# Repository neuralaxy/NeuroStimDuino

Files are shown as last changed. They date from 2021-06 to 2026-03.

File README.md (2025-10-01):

# NeuroStimDuino
An open source neurostimulator for students, researchers, and hobbyists interested in neuroscience

## Update for 2025 - NeuroStimDuino v3.0  launched!! :boom: :boom: 💫
Hello NeuroStim Enthusiats!! Its been a while....over the last year, we have been busy revising the design of NeuroStimDuino. The main reason for modifying NSDuino2.1 was that one of its crucial components, the high voltage DC-DC converter NMT0572SC from Murata has now became obsolete and out of circulation. Sadly, there was no alternative component that could take its place and we spend months trying to find a replacement. 

Finally we had a breakthrough, and we found another DC-DC converter IH0524 from XP Power. We had to redesign the board slightly to incorporate this Converter. But the *downside* is that the new converter only allows a compliance voltage of 35V instead of 60V available in the previous versions. How will this effect your experiments? Well, it means that now you will have to take extra effort in minimizing the skin impedance to deliver higher currents. But we have tried stimulating our arm muscles using this newer version, and it is just as effective as before. And we highly recommend using hydrogel electrodes, as we have suggested before in the [Zucchini](https://www.crowdsupply.com/neuralaxy/neurostimduino/updates/tips-on-electrode-placement) experiment. 

On the *upside*, while we were redesigning the board, we replaced the manual High Voltage slide switch with an electronic switch (see below). So now, you don't have to worry about turning ON the high voltage switch before activating the stimulator. Whenever you give the STIM command, the microcontroller will automatically turn ON the high voltage supply and once the stimulation is turned off, the high voltage supply is automatically turned off. Another benefit of adding the electronic switch is that it will minimize power consumption, since the high-voltage supply doesn't need to be always ON. Now that's smart😎.

Replaced_Slide_Switch_with_SSR

All the other features from NSDuino2.1, like ramping stimulation intensity, touchproof conenctors, etc. have been carried over to NSDuino3.0. Late in September 2025, we launched NeuroStimDuino v3.0 abd shipped out the first batch to our distributor Mouser. A big shout out to 📢 CrowdSupply and Mouser for consistently supporting us over the years. Some of you might have already received the newer version. Try it and let us know how it goes.  

## Important update for 2023
In January 2023 we have launched NeuroStimDuino v2.1, which comes with additional features and improved functionality than its predecessor NeuroStimDuino v1.0. 

NeuroStimDuino_v2 1

Here is a list of important upgrades for NeuroStimDuino v2.1 (NSDuino2.1): 
* Choosing between symmetrical and asymmetrical waveform shapes is now done entirely in software. In NeuroStimDuino v1.0, to switch from symmetrical to asymmetrical waveform, you had to change the jumper (J5, J6) as well as call the `SYMM` command. In NSDuino2.1, its handled entirely by software and the jumpers have been removed. In the default asymmetrical output mode, the anodic phase's amplitude is half of cathodic phase's amplitude and the duration of anodic phase is double that of the cathodic phase (to ensure charge balance). This ratio can be changed by modifying the firmware.

* NSDuino2.1's I<sup>2</sup>C address is now stored on EEPROM. So, whenever you assign a new I<sup>2</sup>C address to NSDuino2.1 using the `ADDR` command, it will get stored permanently and will be recalled at power-on reset. This is especially helpful when communicating with multiple NeuroStimDuinos. In NeuroStimDuino v1.0, the address would reset to the default value (0x1A) everytime the board was turned on and you would have to painstakingly re-assign the new addresses each time. With NSDuino2.1 the new address only needs to be set once and it will store it on-board its EEPROM.

* Many of NeuroStimDuino v1.0 users (who are acutally scientists!!) have asked whether it is possible to ramp up and down the stimulation intensity? Ramping is used in neurostimulation research to avoid painful sensations allow smoother transitions between movements when applying electrical stimulation. With NSDuino2.1, we have also expanded our software (Arduino) library and now provide the option to Ramp Up and Down the stimulation intentsity. When you enable ramping by using the command `RAMP 1`, the stimulation intensity will gradually increase from 0 to the desired level over a 1 second interval. At the end of stimulation, the stimulation intensity will gradually decrease to zero over a 1 second interval. There are some caveats to using ramping: 
  * In the scientific literature, ramping is usually done by increasing/decreasing the current amplitude. While this is doable, by changing the counts of our on-board digital potentiometer, it would require multiple SPI calls between the MCU and potentiometer which will introduce delays. Instead, we are performing ramping by gradually increasing the stimulation pulse-width. This is handled entirely by the MCU and hence it is more accurate. Additionally, it has the same effect as changing the stimulation current, so it won't affect the outcomes of your experiments. Refer to the below gif to understand how ramping essentially works:
  
  NSDuino_Ramping_gif
  
  * Currently, ramping only works for finite stimulation intervals. This means the `Stim Indefinitely` flag of the `STIM` command must be set to `FALSE`. An example code snippet is as follows:
  
  ```
  RAMP 1          // Turn ON ramping on channels 1 & 2
  STIM 1 5 0      // Stimulate on channel 1 for 5 sec, stim indefinitely flag = 0
  RAMP 0          // Turn OFF ramping on channels 1 & 2
  ```
  * Ramping can also be deployed in NeuroStimDuino v1.0. This would require a firmware update. We will post an upgraded firmware for NeuroStimDuino v1.0 on our repository in a few weeks time. Feel free to reach out to us for any queries regarding ramping

* Additional minor modifications:
  * We removed the bi-color(red/green) LEDs to indicate when channels 1 and 2 are stimulating, with regular monocolor LEDs. These still function in the same way
  
  LEDs_changed

  * We changed the onboard cable connectors for Channels 1 & 2 with new ones that are compatible with our stimulation cables and you no longer need to remove the cable shroud or sheath cover. This will hopefully help reduce the hassle during setup and the touchproof connectors will offer additional safety during use.
  
connector_with_shroud

# Getting Started Tutorial for NeuroStimDuino v2.1
**_Important:_** For instructions on getting started with NeuroStimDuino v1.0, please click [here](https://github.com/neuralaxy/NeuroStimDuino/blob/main/NeuroStimDuino%20v1.0%20Getting%20Started.md#getting-started-tutorial-for-neurostimduino-v10)

* To get started, first and foremost familiarize yourself with NeuroStimDuino pinout and board layout below:

NeuroStimDuino_v21_Pinout_Diagram png

NeuroStimDuino_v21_Components png

* If you have ordered the NeuroStimDuino board (without the accessory pack), then you will have received the following components.

package_contents_v2 1

* You also need to order a pair of hydrogel electrodes (from any retail vendor) if you plan to stimulate a fake muscle (such as a [Zucchini](https://www.crowdsupply.com/neuralaxy/neurostimduino/updates/tips-on-electrode-placement)) or for your research.

* Finally, before you begin, please remember to review the **safety guidelines** listed at the [end](https://github.com/neuralaxy/NeuroStimDuino/blob/main/README.md#important-safety-guidelines) of this tutorial and follow the recommendations mentioned therein.  

## Hardware Setup
* The battery holder included requires two 18650 Li-ion batteries (not included) to be connected in series. The battery holder allows the batteries to be oriented in series or parallel connection. Unfortunately, the battery holders we shipped only have Chinese labels to indicate the series or parallel oritentation. Make sure you connect the batteries in series (as shown below) and not in parallel. Alternately, you can power NeuroStimDuino using your own battery source between 6-20V. We do not recommend powering NeuroStimDuino using an AC-DC adapter. However, if you must use an adapter, then you need an adapter with atleast 2 Amps output rating

battery_holder

* The High-Voltage Power Switch S3 turns ON/OFF the +/-72V DC-DC converter (NMT0572SC). When using NeuroStimDuino for the first time we recommend starting with the switch in OFF position. Afterwards, once you are ready to stimulate then flip the switch ON. That way even if you accidentally turn ON the stimulation, it will not have any effect because the high-voltage source will be OFF. Plus it will also help extend battery life. 

power_switch

* To control NeuroStimDuino using an Arduino Due or Mega, stack NeuroStimDuino on top of the Arduino board by aligning the hearder pins, as shown below.



* Once the hardware setup is complete, the amber or yellow Emergency-OFF LED will remain continuously ON. Also TEST_LED1 and TEST_LED2 will start blinking at a rate of 5 blinks per sec.



## Software Setup
* Next, you will need to download the latest version of our [Arduino library](https://github.com/neuralaxy/NeuroStimDuino/tree/main/Software/NeuroStimDuino). Read the full update [here](https://www.crowdsupply.com/neuralaxy/neurostimduino/updates/arduino-library-released) and remember to install the [SerialCommands library] (https://github.com/ppedro74/Arduino-SerialCommands) from Pedro Pereira. Next, upload the example code NeuroStimDuino_SerialControl.ino onto the Arduino.  

* To write instructions to control NeuroStimDuino, you will use the Serial terminal that is in-built Arduino IDE (Tools > Serial Monitor). Once you open the Serial Monitor, set the baudrate to 115200 bps and add "CR+LF" at the end of each command. When you power either the Arduino or NeuroStimDuino board via the DC plug, you will see test LEDs 1 & 2 flashing on the NeuroStimDuino board. These LEDs are flashing with the default stimulation frequency of 10Hz. Now you can enter some example commands into the Serial Monitor, one command at a time and then press enter.

* After uploading the example code NeuroStimDuino_SerialControl.ino and making the connections as above, when you first open the Serial terminal you will see the following welcome message. This mean that a successful connection between Arduino and NeuroStimDuino has been established. It will also give a readout of the current stimulation parameters for each channel. 

Welcome_message

* You can type in some example commands into Serial Monitor and change the settings for the stimulator (type one statement at a time). Also, the commands are case-sensitive, so type it in all caps. 
```
FREQ 1 20        // This will set Channel 1's frequency at 20Hz. You will see the TEST LED1 blink at this new frequency
FREQ 2 50        // This will set Channel 2's frequency at 50Hz. You will see the TEST LED1 blink at this new frequency
AMPL 1 15        // Set Channel 1 intensity 15mA
DURN 1 500       // Set Channel 1 pulse duration at 500 uSec
ENAB 1 1         // This will enable Channel 1 of the stimulation. By default, both channels are enabled at reset
STIM 1 20 0      // This command will turn on stimulation on Channel 1 for 20 seconds. Ensure that the High Voltage Power Switch is ON. 
                 // You will see a Red-Green LED (labelled Ch. 1) blink  very briefly (for 500us), every time the stimulation is generated (i.e, 20  times/sec)
```

## Moving forward

* This completes this introductory tutorial. From here on, if you would like to connect cables and electrodes and actuatlly stimulate a fake Zucchini muscle, then follow the setup instructions shown in our [April Update](https://www.crowdsupply.com/neuralaxy/neurostimduino/updates/tips-on-electrode-placement) published on CrowdSupply. 

* If you want connect multiple NeuroStimDuinos together and control them using a single Arduino, then look up the steps and instructions posted [earlier](https://www.crowdsupply.com/neuralaxy/neurostimduino/updates/controlling-multiple-neurostimduinos-on-a-single-i2c-bus). Note that with NeuroStimDuino_v2.1, when you change the board's I<sup>2</sup>C using the `ADDR` command, the new address is saved on-baord its EEPROM and will be recalled even after reset. It is the User's responsiblity to reset the default I<sup>2</sup>C to `0x1A` if they wish to. 
 
* <br />**One important change** required in hardware when stacking 2 or more NeuroStimDuinos is to disconnect pins 5 & 6 on JP3. Another way to identify these pins is that they normally connect with PWM pins 9 and 10 on Arduino Due or Mega. The reason for this is that these pins can also be used to drive TEST_LED1 and TEST_LED2 of NeuroStimDuino. Therefore, if you connect them together on 2 NeuroStimDuinos, the LEDs will not function properly and can be confusing. Hence, to avoid any cross-talk, its best to fold these pins out of the way as shown below.



* We hope you enjoy tinkering with NeuroStimDuino and use it for all your neuroscience experiments. If you face any issue with the device or are stuck anytime, feel free to write to us on contactus@neuralaxy.com or submit an issue here. 

## Important safety guidelines:
* NeuroStimDuino is not an FDA approved product for clinical use and it is intended for **RESEARCH PURPOSES ONLY**. 
* NeuroStimDuino is not intended for human use or animal use, without receiving prior approval from a local ethics committee such as Institutional Review Boards and Institutional Animal Care and Use Committees  
* Under no circumstances, should the stimulation electrodes be placed across the chest or close to the heart
* NeuroStimDuino requires an external DC input voltage from 6-20V to operate. We **strongly** recommend to use an external battery for this and avoid the use of an AC adapter or anything that's plugged into the AC mains
--->

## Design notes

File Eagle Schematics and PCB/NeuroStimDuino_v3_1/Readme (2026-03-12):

Eagle schematics, BOM and assembly files for version 3.0 of NeuroStimDuino

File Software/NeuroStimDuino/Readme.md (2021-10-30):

## I2C Library for NeuroStimDuino
NeuroStimDuino can be controlled by an external microcontroller such as Arduino Due or Mega using the I2C interface, with NeuroStimDuino acting as I2C slave device (default address = 0x1A). Pull-up resistors for I2C communication are already placed onboard NeuroStimDuino and hence additional pull-up resistors are not required. A list of Opcode-style commands can be used to configure different parameters of stimulation waveform such as frequency, amplitude, etc. Each I2C message should have following structure:

- Byte 0 indicates the number of bytes that will be transferred
- Byte 1 is the Opcode command from the instruction set below for the stimulation parameter that will be modified
- Byte 2 is the channel number (1 or 2) that will written to or read from
- Byte 3 is the LSB byte of the value written
- Byte 4 is the MSB byte of the value written

## Instruction Set 
| **Instruction** | **Address** | **Description** | **Acceptable Range** | 
|----------------|--------------|-----------------|------------------------|
|  AMPL |  0x01 |   Change stimulation amplitude | 0 - 25, Unit: milliAmps |
|  FREQ  |  0x02 |   Change stimulation frequency | 1 - 100, Unit:  Hz |
|  DURN |  0x03 |  Change pulse-duration of the cathodic pulse. | 0 - 2000, Unit: uSec. |
|  IDLY | 0x04 | Change inter-phase delay | 0 - 255, Unit: uSec. |
|  DELY | 0x05 | Delay to the start of the stimulation pulse in each cycle | 0 - 1/(stimulation frequency), Unit: mSec.|
|  SYMM | 0x06 | Generate symmetrical or asymmetrical stim waveform <br /> (*Note: Make sure to change jumpers J5 and J6 settings on the board*) | 1 = Symm.; 0 = Asymm. |
|  ADDR  | 0x07 | Change 7-bit I2C address | Allowed addresses = 0x08 - 0x77; <br /> program/switch_only flag = 1/0|
|  SAMP  | 0x08 | Sample current on channel 1 or 2 | - |
|  READ  | 0x09 | Read value of register for specified channel <br /> Usage: READ Channel# Address <br /> (e.g. To read amplitude of Channel 1, use "READ 1 AMPL")   | - |
|  RSET  | 0x0A | Reset NeuroStimDuino to default register values | - |
|  EOFF | 0x0F | Generate Emergency Off condition | - |
|  STIM | 0x10 | Start stimulation on channel 1 or 2 for finite duration or stimulate indefinitely <br /> Usage: STIM Channel# Seconds# Stim Indefinitely <br /> (e.g. To stimulate on Channel 1 for 5 seconds, use "STIM 1 5 0") | 0 - 255 Sec; <br /> Stim indefinitely flag = 1/0| 
|  STOP | 0x12 | Stop stimulation on channel 1 or 2 | - | 
|  ENAB | 0x14 | Enable or disable a stim. channel | 1 = Enable; 0 = Disable | 
|  WAIT  | 0x20 | Idle | - |

## Arduino Example
An example sketch is included: NeuroStimDuino_SerialControl.ino to send I2C commands to NeuroStimDuino over the serial port. Set the baudrate at 115200 bps and add "CR+LF" at the end of each command. For using this library, you will need to install SerialCommands library available from Pedro Pereira at https://github.com/ppedro74/Arduino-SerialCommands. The library will automatically switch between SDA, SCL pins (Wire) for Arduino MEGA256 and SDA1,SCL1 pins (Wire1) for Arduino Due. 

**Some examples of Commands sent over COM port** <br />
* AMPL 1 15     &nbsp;&nbsp;&nbsp;&nbsp;&nbsp;&nbsp; // Set Channel 1 intensity at 15mA
* FREQ 1 20     &nbsp;&nbsp;&nbsp;&nbsp;&nbsp;&nbsp; // Set Channel 1 frequency at 20Hz
* DURN 1 500    &nbsp;&nbsp;&nbsp;&nbsp; // Set Channel 1 pulse duration at 500 uSec
* STIM 1 20 0   &nbsp;&nbsp;&nbsp;&nbsp; // Turn on Channel 1 for 20 seconds
* STIM 1 20 1   &nbsp;&nbsp;&nbsp;&nbsp; // Turn on Channel 1 indefinitely

## Measure Stimulation Output
Using an on-baord current sense amplifier you can measure the stimulation output as shown below - 

Symmetrical_Asymm_Outputs_500us
Signal traces were obtained above by averaging 10 trials for each amplitude setting, in order to minimize background noise.

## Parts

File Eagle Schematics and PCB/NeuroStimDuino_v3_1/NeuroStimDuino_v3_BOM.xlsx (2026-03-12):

Qty | Value | Device | Package | Parts | Description | Column1 | _1
3 | 0.1uF | CGA4J2X7R2A104K125AA | C0805K | C1, C39, C40 | CAPACITOR, American symbol
1 | 56nF | C0603C563J4RACTU | CAPC17595_87N_KEM | C11
9 | 1uF | C0805C105K3RACTU | C0805 | C13, C15, C26, C31, C32, C35, C36, C37, C38 | CAPACITOR, American symbol
1 | 4.7uF | F971C475MAAHT3 | CAPPM3216X180N | C2 | Tantalum Capacitors - Solid SMD 16V 4.7uF 20% 1206 ESR=4Ohm AEC-Q200
1 | 10uF | C2012X7S1E106K125AE | C0805 | C27 | CAPACITOR, American symbol
1 | 47uF | 865230445005 | Wurth Electronik | C29 | 47uF
11 | 0.1uF | C1206C104K3RACTU | C1206 | C3, C4, C5, C7, C8, C9, C12, C14, C19, C21, C25 | CAPACITOR, American symbol
2 | 10nF | CGA5H4X7R2J103K115AA | C1206 | C6, C28 | CAPACITOR, American symbol
1 | SS1P3L | 0025_SS1P3L-M3/84A | DO220AAL | D2 | 1A 30V Schottky Barrier Rectifiers -SS1P3L-M3/84A
1 | MSS1P3L-M3/89A | 1653_MSS1P3L-M3/89A | MICROSMP | D3 | Surface Mount Schottky Barrier Rectifiers - Case microSMP
2 | LSM115JE3_TR13 | LSM115JE3_TR13 | DIOM5436X330N | D4, D5 | Schottky Diodes & Rectifiers Schottky
4 | GF1J-E3DO-214BA-L | GF1J-E3DO-214BA-L | DO-214BA-L | D6, D7, D8, D9
2 | 0453.062MR | 0453.062MR | FUSC6127X294N | F2, F3 | Surface Mount Fuses 125VAC 0.062A 5.5ohms 453 NANO2
1 | ACSL-6410-00TE | ACSL-6410-00TE | SOIC127P599X152-16N | IC11 | Broadcom ACSL-6410-00TE DC Input Logic Gate Output Quad Optocoupler, Surface Mount, 16-Pin SOIC-N
1 | MCP6479-E_ST or TS274IPT | MCP6479-E_ST or TS274IPT | SOP65P640X120-14N | IC12 | Operational Amplifiers - Op Amps Quad, 3MHz Op Amp, E Temp
1 | TPS73633DBVR | TPS73633DBVR | SOT95P280X145-5N | IC13 | Single Output LDO, 400mA, Adj.(1.2 to 5.5V), Cap free, Low Noise, Reverse Current Protection
1 | MIC3975-5.0YMM-TR | MIC3975-5.0YMM-TR | SOP65P490X109-8N | IC14 | ic
1 | DSPIC33FJ64GS606-I_PT | DSPIC33FJ64GS606-I_PT | QFP50P1200X1200X120-64N | IC15 | Microchip DSPIC33FJ64GS606-I/PT, 16bit PIC Microcontroller, 40MHz, 64 kB Flash, 64-Pin TQFP
2 | HCPL0531 | HCPL0531 | SOIC127P594X363-8N | IC3, IC4 | Optocoupler 2-Ch Transistor 1MBit/s SO8
2 | AD629ARZ-R7 or INA149AID | AD629ARZ-R7 or INA149AID | SOIC127P600X175-8N | IC5, IC8 | Texas Instruments INA149AID, Differential Amplifier 8-Pin SOIC
1 | TSC2012IST | TSC2012IST | SOP65P490X110-8N | IC6 | SP Amp Current Sense Amp Single 5.5V 8-Pin Mini-SO T/R
2 | OPA140AID | OPA140AID | SOIC127P600X175-8N | IC7, IC10 | 11MHz, Single Supply, Low Noise, Precision, Rail-to-Rail Output, JFET Amplifier
1 | MCP4341-103E_ST | MCP4341-103E_ST | SOP65P640X120-20N | IC9 | 7 bit Digital Potentiometers, 10k, SPI
1 | 22-27-2051-05 | 22-27-2051-05 | 6410-05 | J1 | CONNECTOR
2 | Custom Connector | DC_JACK_081BB-2103300 | 081BB-2103300 | J3, J4
1 | CON-SOCJ-2155 | CON-SOCJ-2155 | CONSOCJ2155 | J7 | DC Power Connectors Power Jack/Connector 2.1mm x 5.5mm
1 | Stackable Header - 2 Pin |  | 1X02 | JP2 | Female Gray Connecter strip 2x1 F V h 8,5 p2,54mm
1 | Stackable Header - 10 Pin | https://robu.in/product/10-pin-female-11mm-tall-stackable-header-connector/ | 1X10 | JP3 | Female Gray Connector strip for Arduino 3V3 bases - 10x1 F V h 8,5 p2,54mm
3 | Stackable Header - 8 Pin | https://robu.in/product/8-pin-female-11mm-tall-stackable-header-connector-for-arduino-5pcs/ | 1X08 | JP4, JP5, JP6 | Female Gray Connector strip for Arduino 3V3 bases - 8x1 F V h 8,5 p2,54mm
1 | CPC2125N | CPC2125N | SOP254P610X218-8N | K1 | Solid State Relays - PCB Mount Dual SP-NC SS OptoMOS Relay
1 | LCA717S_DC | LCA717S_DC | SOP254P952X470-6N | K2 | Solid State Relays - PCB Mount 1-Form 30V 2000 mA Solid State Relay
1 | BLM21PG300SN1D | BLM21PG300SN1D | 0805 | L1 | BLM21
4 | LED | APTR3216SGC | CHIPLED_1206 | LED5, LED6, LED7, LED8 | LED
2 | IH0524D or IH0524SH | IH0524D or IH0524SH | IH0524D or IH0524SH | PS4, PS6 or PS1, PS7 | Isolated DC/DC Converters DC-DC, 2W, unreg., dual output, SIP, 3kV
1 | TEA_1-0505 | TEA_1-0505 | TEA10505 | PS3 | 1 Watt DC/DC converter, industrial, +/-10% input, unregulated, highly cost efficient, encapsulated, SIP-4
2 | MJE350 | MJE350 | TO229P300X760X1364-3P | Q1, Q3 | Source: Datasheet
2 | MJE340 | MJE340 | TO229P290X760X1320-3P | Q2, Q4 | MJE340, NPN Bipolar Transistor, 0.5 A 300 V HFE:30 V Power, 3-Pin SOT-32
1 | MMBT3906 | MMBT3906 | SOT95P240X120-3N | Q8 | Transistor GP BJT PNP 40V 0.2A SOT23 Fairchild MMBT3906 PNP Bipolar Transistor, 0.2 A, 40 V, 3-Pin SOT-23
1 | 10K | RC0805FR-0710KL | R0805 | R1 | RESISTOR, American symbol
1 | 0.5E | RCWE1206R500FKEA | R1206 | R10 | RESISTOR, American symbol
4 | 35.7K | RT1206FRE0735K7L | R1206 | R11, R14, R18, R21 | RESISTOR, American symbol
4 | 10K, 1/2W | RCS120610K0JNEA | R1206 | R12, R13, R19, R20 | RESISTOR, American symbol
2 | 100E, 1/2W | MCA1206MD1000BP100 | R1206 | R15, R22 | RESISTOR, American symbol
2 | 10E, 3/4W | CRCW120610R0FKEBHP | R1206 | R16, R23 | RESISTOR, American symbol
1 | 3.3K | ERJ-8ENF3301V | R1206 | R17 | RESISTOR, American symbol
1 | 470E | ERJ-8ENF4700V | R0805 | R2 | RESISTOR, American symbol
5 | 330E | ERJ-UP3J331V | R0603 | R26, R27, R28, R29, R30 | RESISTOR, American symbol
2 | 10K | CRGH1206F10K | R1206 | R3, R4 | RESISTOR, American symbol
1 | 100E | R_0805 | R0805 | R31 | RESISTOR
1 | 100K | ERJ-UP8F1003V | R1206 | R32 | RESISTOR, American symbol
1 | 470K | ERJ-UP8F4703V | R1206 | R33 | RESISTOR, American symbol
1 | 220E | ERJ-8ENF2200V | R1206 | R34 | RESISTOR, American symbol
2 | 330E | R-US_R1206 | R1206 | R36, R37 | RESISTOR, American symbol
1 | 4605X-101-221LF | 4605X-101-221LF | BO_4605X | R8
1 | 4605X-101-332LF | 4605X-101-332LF | BO_4605X | R9
1 | CAY16-332J4LF | CAY16-332J4LF | CAY16-J4 | RN1 | Bourns CAY16 Series 3.3k +/-5% Isolated SMT Resistor Array, 4 Resistors, 0.25W total 1206 (3216M) package Convex
1 | CAY16-181J4LF | CAY16-181J4LF | CAY16181J4LF | RN2 | BOURNS - CAY16-181J4LF - Fixed Network Resistor, 180 ohm, Isolated, 4 Elements, 1206 [3216 Metric], 8 Pins, Convex
1 | PTS525SM15SMTR2 LFS | PTS525SM15SMTR2 LFS | TACTILE_SWITCH_SMD | S1
1 | 3006.2115 or 3006.2101 | 3006.2115 or 3006.2101 | 30062115 | S2 | Tactile Switches TACTILE
1 | LTC4412HS6TRMPBF | LTC4412HS6TRMPBF | TSOT-23_S6_ADI | U6
1 | PMV48XP,215 | PMV48XP,215 | TO-236_SOT23_NEX-L | U7
1 | MAX6018BEUR16+T | MAX6018BEUR16+T | 21-0051H_MXM | U9
114 |  |  |  |  |  |  | 62

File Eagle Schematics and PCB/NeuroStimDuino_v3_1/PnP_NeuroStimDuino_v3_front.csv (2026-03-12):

C13 | 45.97 | 7.11 | 180 | 1uF | C0805
C15 | 52.07 | 7.11 | 180 | 1uF | C0805
C26 | 21.79 | 7.01 | 90 | 1uF | C0805
C27 | 30.36 | 6.28 | 0 | 10uF | C0805
C29 | 16.15 | 14.82 | 180 | 47uF | PANASONIC_D
C35 | 78.99 | 30.75 | 180 | 1uF | C0805
C36 | 64.77 | 30.75 | 180 | 1uF | C0805
C37 | 78.99 | 37.35 | 180 | 1uF | C0805
C38 | 64.51 | 37.86 | 180 | 1uF | C0805
C39 | 42.16 | 38.37 | 180 | 100nF | C0805K
C40 | 57.91 | 37.86 | 180 | 100nF | C0805K
C6 | 10.49 | 21.01 | 180 | 10nF | C1206 |  | DNP
D2 | 17.5 | 8.25 | 180 | SS1P3L | DO220AAL
D3 | 17.63 | 5.91 | 180 | MSS1P3L-M3/89A | MICROSMP
D4 | 15.74 | 22.37 | 90 | LSM115JE3_TR13 | DIOM5436X330N
D5 | 21.84 | 2.3 | 0 | LSM115JE3_TR13 | DIOM5436X330N
D6 | 41.14 | 31.13 | 0 | GF1J-E3DO-214BA-L | DO-214BA-L
D7 | 33.27 | 31.13 | 0 | GF1J-E3DO-214BA-L | DO-214BA-L
D8 | 56.91 | 31.06 | 0 | GF1J-E3DO-214BA-L | DO-214BA-L
D9 | 48.91 | 31.06 | 0 | GF1J-E3DO-214BA-L | DO-214BA-L
F1 | 2.99 | 29.89 | 270 | MF-MSMF050-2 500mA | L1812 |  | DNP
F2 | 94.93 | 7.77 | 0 | 0453.062MR | FUSC6127X294N
F3 | 94.9 | 24.38 | 0 | 0453.062MR | FUSC6127X294N
IC10 | 49.42 | 18.74 | 0 | OPA140AID | SOIC127P600X175-8N
IC14 | 31.31 | 10.45 | 0 | MIC3975-5.0YMM-TR | SOP65P490X109-8N
IC5 | 37.21 | 25.67 | 0 | INA149AID | SOIC127P600X175-8N
IC7 | 34.16 | 18.81 | 0 | OPA140AID | SOIC127P600X175-8N
IC8 | 52.85 | 25.48 | 0 | INA149AID | SOIC127P600X175-8N
IC9 | 49.96 | 43.61 | 270 | MCP4341-103E_ST | SOP65P640X120-20N
J2 | 2.58 | 22.2 | 90 | 47346-0001 | 47346-0001 |  | DNP
K2 | 6.1 | 48.26 | 0 | LCA717S_DC | SOP254P952X470-6N
L1 | 14.63 | 7.89 | 90 | MH2029-300Y | 805
LED1 | 22.22 | 29.99 | 180 |  | CHIPLED_1206 |  | DNP
LED2 | 19.82 | 29.94 | 180 |  | CHIPLED_1206 |  | DNP
LED5 | 28.44 | 41.42 | 270 |  | CHIPLED_1206
LED6 | 29.97 | 39.39 | 90 |  | CHIPLED_1206
LED7 | 76.71 | 46.48 | 90 |  | CHIPLED_1206
LED8 | 75.69 | 44.2 | 90 |  | CHIPLED_1206
Q8 | 83.31 | 45.74 | 0 | MMBT3906 | SOT95P240X120-3N
R11 | 69.34 | 30.75 | 0 | 35.7K | R1206
R12 | 33.52 | 34.94 | 180 | 10K | 1/2W | R1206
R13 | 41.65 | 35.07 | 0 | 10K | 1/2W | R1206
R14 | 83.56 | 30.62 | 180 | 35.7K | R1206
R15 | 42.16 | 18.81 | 90 | 100E | 1/2W | R1206
R17 | 84.57 | 41.65 | 0 | 3.3K | R1206
R18 | 69.23 | 37.92 | 0 | 35.7K | R1206
R19 | 49.38 | 34.76 | 180 | 10K | 1/2W | R1206
R20 | 57.51 | 34.88 | 0 | 10K | 1/2W | R1206
R21 | 83.67 | 37.3 | 180 | 35.7K | R1206
R22 | 60.8 | 24.19 | 180 | 100E | 1/2W | R1206
R26 | 24.13 | 40.4 | 180 | 330E | R0603
R27 | 33.27 | 41.42 | 0 | 330E | R0603
R3 | 16.51 | 39.39 | 270 | 10K | R1206
R32 | 26.61 | 7.8 | 90 | 100K | R1206
R33 | 21.74 | 13.1 | 270 | 470K | R1206
R34 | 95.75 | 50.31 | 0 | 220E | R1206
R4 | 19.55 | 39.39 | 270 | 10K | R1206
R5 | 17.22 | 30.14 | 270 | 330E | R1206 |  | DNP
R7 | 24.72 | 30.01 | 270 | 330E | R1206 |  | DNP
S1 | 3.25 | 39.01 | 270 | SWITCH-MOMENTARY-2SMD | TACTILE_SWITCH_SMD
S2 | 92.45 | 42.43 | 0 | 3006.2115 | 30062115
U6 | 8.6 | 14.9 | 90 | LTC4412HS6TRMPBF | TSOT-23_S6_ADI
U7 | 4.18 | 15.92 | 90 | PMV48XP | 215TO-236_SOT23_NEX-L | TO-236_SOT23_NEX-L

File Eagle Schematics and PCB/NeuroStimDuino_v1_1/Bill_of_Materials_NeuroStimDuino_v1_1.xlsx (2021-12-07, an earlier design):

Qty | Parts | Value | Device | Package | Description
11 | C1, C3, C4, C5, C7, C8, C13, C14, C19, C21, C25 | 0.1uF | C1206C104K3RACTU | C1206 | CAPACITOR, American symbol
5 | C2, C9, C10, C17, C18 | 4.7uF | F971C475MAAHT3 | C1206 | Tantalum Capacitors - Solid SMD 16V 4.7uF 20% 1206 ESR=4Ohm AEC-Q200
7 | C26, C31, C32, C35, C36, C37, C38 | 1uF | C0805C105K3RACTU | C0805 | CAPACITOR, American symbol
1 | C11 | 56nF | C0603C563J4RACTU | C0603 | CAPC17595_87N_KEM
1 | C27 | 10uF | CGA4J1X7S1E106K125AC | C0805 | CAPACITOR, American symbol
1 | C29 | 47uF | EEE-FK1E470V | PANASONIC_D | 47uF
3 | C30, C33, C34 | 4.7uF | 293D475X9050D2TE3 | CAPPM7343X310N | Solid Tantalum Surface Mount Chip Capacitors TANTAMOUNT(TM), Molded Case, Low ESR
2 | C39, C40 | 100nF | CGA4J2X7R2A104K125AA | C0805 | CAPACITOR, American symbol
1 | C28 | 10nF | CGA5H4X7R2J103K115AA | C1206 | CAPACITOR, American symbol
1 | D2 | SS1P3L | SS1P3L-M3/84A | DO220AAL | 1A 30V Schottky Barrier Rectifiers -SS1P3L-M3/84A
1 | D3 | MSS1P3L-M3/89A | MSS1P3L-M3/89A | MICROSMP | Surface Mount Schottky Barrier Rectifiers - Case microSMP
2 | D4, D5 | LSM115JE3_TR13 | LSM115JE3_TR13 | DIOM5436X330N | Schottky Diodes & Rectifiers Schottky
4 | D6, D7, D8, D9 | GF1J-E3/67A | GF1J-E3/67A | DO-214BA-L
2 | F2, F3 | 0453.062MR | 0453.062MR | 0453.062MR | Surface Mount Fuses 125V .062A
1 | IC1 | DSPIC33FJ256GP506A-I_PT | DSPIC33FJ256GP506A-I_PT | QFP50P1200X1200X120-64N | MCU&DSP 256K Flash 16K RAM DMA TQFP64
1 | IC13 | TPS73633DBVR | TPS73633DBVR | SOT95P280X145-5N | Single Output LDO, 400mA, Adj.(1.2 to 5.5V), Cap free, Low Noise, Reverse Current Protection
1 | IC14 | MIC3975-5.0YMM-TR | MIC3975-5.0YMM-TR | SOP65P490X109-8N | ic
2 | IC3, IC4 | HCPL0531 | HCPL0531 | SOIC127P594X363-8N | Optocoupler 2-Ch Transistor 1MBit/s SO8
2 | IC5, IC8 | INA149AID/AD629ARZ-R7 | INA149AID | SOIC127P600X175-8N | Texas Instruments INA149AID, Differential Amplifier 8-Pin SOIC
1 | IC6 | TSC2012IST | TSC2012IST | SOP65P490X110-8N | SP Amp Current Sense Amp Single 5.5V 8-Pin Mini-SO T/R
2 | IC7, IC10 | OPA140AID | OPA140AID | SOIC127P600X175-8N | 11MHz, Single Supply, Low Noise, Precision, Rail-to-Rail Output, JFET Amplifier
1 | J1 | 22-27-2051 | 22-27-2051 | Molex | CONNECTOR
2 | J3, J4 | PJ1-022 | PJ1-022 | PJ1-022 | WR-DC DC Power Jack THT Right Angled Low Profile (2.8)
2 | J5, J6 | TMS-103-02-G-S | TMS-103-02-G-S | TMS-103-YY-XX-S | 3 Position, Single-Row .050" x .100" Micro Terminal Strip
1 | J7 | CON-SOCJ-2155 | CON-SOCJ-2155 | CONSOCJ2155 | DC Power Connectors Power Jack/Connector 2.1mm x 5.5mm
1 | JP3 | PRT-11376 | PRT-11376 | Sparkfun | Female Gray Connector strip for Arduino 3V3 bases - 10x1 F V h 8,5 p2,54mm
4 | JP4, JP5, JP6, JP7 | LS-00008 | LS-00008 | OSEPP Electronics | Female Gray Connector strip for Arduino 3V3 bases - 8x1 F V h 8,5 p2,54mm
1 | JP8 | PRT-09279 | PRT-09279 | Sparkfun
1 | K1 | LBB110P | LBB110P | SOP254P940X229-8N | Solid State Relays - PCB Mount 350V 120mA Dual Sing OptoMOS Relay
1 | L1 | BLM21PG300SN1D | BLM21PG300SN1D | L0805 | BLM21
2 | LED5, LED6 | APTR3216SGC | APTR3216SGC | CHIPLED_1206 | LED
2 | LED3, LED4 | XZMDKVG55W-4 | XZMDKVG55W-4 | LED_KVG55W-4_SLD
2 | PS1, PS2 | NMT0572SC | NMT0572SC |  | Murata Power Solutions NMT 3W Isolated DC-DC Converter Through Hole, Vin 4.5 5.5 V dc, Vout -72/-48/-24V dc
2 | Q1, Q3 | MJE350 | MJE350 | TO229P300X760X1364-3P | Source: Datasheet
2 | Q2, Q4 | MJE340 | MJE340 | TO229P290X760X1320-3P | MJE340, NPN Bipolar Transistor, 0.5 A 300 V HFE:30 V Power, 3-Pin SOT-32
1 | Q8 | MMBT3906 | MMBT3906 | SOT95P240X120-3N | Transistor GP BJT PNP 40V 0.2A SOT23 Fairchild MMBT3906 PNP Bipolar Transistor, 0.2 A, 40 V, 3-Pin SOT-23
3 | R1, R3, R4 | 10K | CRGH1206F10K | R1206 | RESISTOR, American symbol
1 | R10 | 0.5E | RCWE1206R500FKEA | R1206 | RESISTOR, American symbol
4 | R11, R14, R18, R21 | 35.7K | RT1206FRE0735K7L | R1206 | RESISTOR, American symbol
4 | R12, R13, R19, R20 | 10K, 1/2W | RCS120610K0JNEA | R1206 | RESISTOR, American symbol
2 | R15, R22 | 100E, 0.4W | MCA1206MD1000BP100 | R1206 | RESISTOR, American symbol
2 | R16, R23 | 10E, 3/4W | CRCW120610R0FKEBHP | R1206 | RESISTOR, American symbol
1 | R17 | 3.3K | ERJ-8ENF3301V | R1206 | RESISTOR, American symbol
1 | R2 | 470E | ERJ-8ENF4700V | R1206 | RESISTOR, American symbol
2 | R26, R28 | 330E | ERJ-UP3J331V | R0603 | RESISTOR, American symbol
1 | R27 | 1K | ERJ-UP3D1001V | R0603 | RESISTOR, American symbol
1 | R32 | 100K | ERJ-UP8F1003V | R1206 | RESISTOR, American symbol
1 | R33 | 470K | ERJ-UP8F4703V | R1206 | RESISTOR, American symbol
1 | R34 | 220E | ERJ-8ENF2200V | R1206 | RESISTOR, American symbol
2 | R36, R37 | 330E | ERJ-8ENF3300V | R1206 | RESISTOR, American symbol
1 | R8 | 4605X-101-221LF | 4605X-101-221LF | BO_4605X
1 | R9 | 4605X-101-332LF | 4605X-101-332LF | BO_4605X
1 | S1 | COM-12992 | Sparkfun
1 | S2 | 3006.2115/3006.2101 | 3006.2115 | 30062115 | Tactile Switches TACTILE
1 | S3 | CS12ANW03 | CS12ANW03 | NKK Switches | Slide Switches
1 | U1 | AD826ARZ | AD826ARZ | R_8_ADI
2 | U2, U3 | LT1991IMSPBF | LT1991IMSPBF | MSOP-10_MS_LIT
2 | U4, U5 | MCP41HV31-103E/ST | MCP41HV31-103E/ST | TSSOP14_MC_MCH
1 | U6 | LTC4412HS6TRMPBF | LTC4412HS6TRMPBF | TSOT-23_S6_ADI
1 | U7 | PMV48XP,215 | PMV48XP,215 | TO-236_SOT23_NEX-L
1 | U8 | PDME1-S5-D5-S | PDME1-S5-D5-S | CONV_PDME1-S5-D5-S | 1 W, 1:1 Input Range, Single/Dual Unregulated Output, SIP, 1500 Vdc Isolation, Dc-Dc Converter
1 | U9 | MAX6018BEUR16+T | MAX6018BEUR16+T | 21-0051H_MXM
2 |  | M50-2000005 | Harwin | CONN JUMPER SHORTING 1.27MM GOLD
119
 |  |  |  | x`

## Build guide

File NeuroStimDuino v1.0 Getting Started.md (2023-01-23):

# Getting Started Tutorial for NeuroStimDuino v1.0
* To get started, first and foremost familiarize yourself with NeuroStimDuino's board layout and pinout below

NeuroStimDuino_Components

NeuroStimDuino_Pinout_Diagram

* If you just ordered the NeuroStimDuino board (without the accessory pack), then you will have received the following components.  
CS_NEUROSTIM_01

* If you have ordered the accessory pack as well, then you will also receive hydrogel electrodes and extra cables (seen below). The hydrogel electrodes are required if you plan to stimulate a fake muscle (such as a [Zucchini](https://www.crowdsupply.com/neuralaxy/neurostimduino/updates/tips-on-electrode-placement)) or for your research.
CS_NEUROSTIM_02

* Finally, before you begin, please remember to review the **safety guidelines** listed at the [end](https://github.com/neuralaxy/NeuroStimDuino/blob/main/README.md#important-safety-guidelines) of this tutorial and follow the recommendations mentioned therein.  

## Hardware Setup
* The battery holder included requires two 18650 Li-ion batteries (not included) to be connected in series. The battery holder allows the batteries to be oriented in series or parallel connection. Unfortunately, the battery holders we shipped only have Chinese labels to indicate the series or parallel oritentation. Make sure you connect the batteries in series (as shown below) and not in parallel. Alternately, you can power NeuroStimDuino using your own battery source between 6-20V. We do not recommend powering NeuroStimDuino using an AC-DC adapter. However, if you must use an adapter, then you need an adapter with atleast 2 Amps output rating

battery_holder

* For connecting the stimulation cables, you will have to remove the cable shroud or sheath cover as shown below and then plug it into the 0.7mm DC Jack.



* Ensure the jumper settings for selecting the shape of the current waveforms are set to "x1" or Symmetrical, as shown below. 

Jumper_setting

* The High-Voltage Power Switch S3 turns ON/OFF the +/-72V DC-DC converter (NMT0572SC). When using NeuroStimDuino for the first time we recommend starting with the switch in OFF position. Afterwards, once you are ready to stimulate then flip the switch ON. That way even if you accidentally turn ON the stimulation, it will not have any effect because the high-voltage source will be OFF. Plus it will also help extend battery life. 

power_switch

* To control NeuroStimDuino using an Arduino Due or Mega, stack NeuroStimDuino on top of the Arduino board by aligning the hearder pins, as shown below.



* Once the hardware setup is complete, the amber or yellow Emergency-OFF LED will remain continuously ON. Also TEST_LED1 and TEST_LED2 will start blinking at a rate of 10 Hz



## Software Setup
* Next, you will need to download the latest version of our [Arduino library](https://github.com/neuralaxy/NeuroStimDuino/tree/main/Software/NeuroStimDuino). Read the full update [here](https://www.crowdsupply.com/neuralaxy/neurostimduino/updates/arduino-library-released) and remember to install the [SerialCommands library] (https://github.com/ppedro74/Arduino-SerialCommands) from Pedro Pereira. Next, upload the example code NeuroStimDuino_SerialControl.ino onto the Arduino.  

* To write instructions to control NeuroStimDuino, you will use the Serial terminal that is in-built Arduino IDE (Tools > Serial Monitor). Once you open the Serial Monitor, set the baudrate to 115200 bps and add "CR+LF" at the end of each command. When you power either the Arduino or NeuroStimDuino board via the DC plug, you will see test LEDs 1 & 2 flashing on the NeuroStimDuino board. These LEDs are flashing with the default stimulation frequency of 10Hz. Now you can enter some example commands into the Serial Monitor, one command at a time and then press enter.

* After uploading the example code NeuroStimDuino_SerialControl.ino and making the connections as above, when you first open the Serial terminal you will see the following welcome message. This mean that a successful connection between Arduino and NeuroStimDuino has been established. It will also give a readout of the current stimulation parameters for each channel. 

Welcome_message

* You can type in some example commands into Serial Monitor and change the settings for the stimulator (type one statement at a time). Also, the commands are case-sensitive, so type it in all caps. 
```
FREQ 1 20        // This will set Channel 1's frequency at 20Hz. You will see the TEST LED1 blink at this new frequency
FREQ 2 50        // This will set Channel 2's frequency at 50Hz. You will see the TEST LED1 blink at this new frequency
AMPL 1 15        // Set Channel 1 intensity 15mA
DURN 1 500       // Set Channel 1 pulse duration at 500 uSec
ENAB 1 1         // This will enable Channel 1 of the stimulation. By default, both channels are enabled at reset
STIM 1 20 0      // This command will turn on stimulation on Channel 1 for 20 seconds. Ensure that the High Voltage Power Switch is ON. 
                 // You will see a Red-Green LED (labelled Ch. 1) blink  very briefly (for 500us), every time the stimulation is generated (i.e, 20  times/sec)
```

## Moving forward

* This completes this introductory tutorial. From here on, if you would like to connect cables and electrodes and actuatlly stimulate a fake Zucchini muscle, then follow the setup instructions shown in our [April Update](https://www.crowdsupply.com/neuralaxy/neurostimduino/updates/tips-on-electrode-placement) published on CrowdSupply. 

* If you want connect multiple NeuroStimDuinos together and control them using a single Arduino, then look up the steps and instructions posted [earlier](https://www.crowdsupply.com/neuralaxy/neurostimduino/updates/controlling-multiple-neurostimduinos-on-a-single-i2c-bus). 
<br />**One important change** required in hardware when stacking 2 or more NeuroStimDuinos is to disconnect pins 5 & 6 on JP3. Another way to identify these pins is that they normally connect with PWM pins 9 and 10 on Arduino Due or Mega. The reason for this is that these pins can also be used to drive TEST_LED1 and TEST_LED2 of NeuroStimDuino. Therefore, if you connect them together on 2 NeuroStimDuinos, the LEDs will not function properly and can be confusing. Hence, to avoid any cross-talk, its best to fold these pins out of the way as shown below.



* We hope you enjoy tinkering with NeuroStimDuino and use it for all your neuroscience experiments. If you face any issue with the device or are stuck anytime, feel free to write to us on contactus@neuralaxy.com or submit an issue here. 

## Important safety guidelines:
* NeuroStimDuino is not an FDA approved product for clinical use and it is intended for **RESEARCH PURPOSES ONLY**. 
* NeuroStimDuino is not intended for human use or animal use, without receiving prior approval from a local ethics committee such as Institutional Review Boards and Institutional Animal Care and Use Committees  
* Under no circumstances, should the stimulation electrodes be placed across the chest or close to the heart
* NeuroStimDuino requires an external DC input voltage from 6-20V to operate. We **strongly** recommend to use an external battery for this and avoid the use of an AC adapter or anything that's plugged into the AC mains

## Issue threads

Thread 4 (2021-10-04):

### ISSUE TITLE
Program compilation and download

### ISSUE THREAD

**Issue by yanwang631** [neuralaxy/NeuroStimDuino#4]
Hi, neuralaxy 
   How to upload the program to the DSP chip？Because I don't have a mega256 or other additional controllers at the moment，can you tell me how to control neurostimduino directly through computer?

**Comment by neuralaxy** [comment]
Hello Yanwang,

Since you have fabricated the board, you will need to upload the firmware
for controlling NeuroStimDuino using USB or an Arduiono. We haven't shared
our firmware yet, pending some final changes and modifications required.
Once, we share the firmware you will have access to it.

Regards,
Neuralaxy LLC

**Comment by yanwang631** [comment]
neuralaxy，Thank you very much for your answer.I know that the firmware is being adjusted and cannot be made public right now. But because my graduate advisor is pushing hard for experiments on electrical stimulation. I use it just to acquire human surface EMG signals in the case of electrical stimulation. It will not be used for commercial or other purposes, so I was wondering if you could please send a version of the firmware first. My email is **694216849@qq.com**. Finally thank you again!

**Comment by yanwang631** [comment]
> Hello Yanwang, Since you have fabricated the board, you will need to upload the firmware for controlling NeuroStimDuino using USB or an Arduiono. We haven't shared our firmware yet, pending some final changes and modifications required. Once, we share the firmware you will have access to it. Regards


neuralaxy，Thank you very much for your answer.I know that the firmware is being adjusted and cannot be made public right now. But because my graduate advisor is pushing hard for experiments on electrical stimulation. I use it just to acquire human surface EMG signals in the case of electrical stimulation. It will not be used for commercial or other purposes, so I was wondering if you could please send a version of the firmware first. My email is 694216849@qq.com. Finally thank you again!

**Comment by neuralaxy** [comment]
Hello @yanwang631 

Sorry for the late response. The .HEX file for dsPIC controller is now available here: https://github.com/neuralaxy/NeuroStimDuino/blob/main/Software/Firmware/NeuroStimDuino.X.production.hex. Instructions for burning the hex file using MPLAB-X are also provided in the comments. 

We will be uploading the source code in a few days as well. Till then you can get started with the HEX file and use it for your project. Hope this is helpful.

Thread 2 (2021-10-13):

### ISSUE TITLE
PDF files for schematic and board

### ISSUE THREAD

**Issue by gaudat** [neuralaxy/NeuroStimDuino#2]
For the us that do not have Eagle installed, can you upload the hardware design files in a more open format? Say PDFs, or Gerbers, or even a KiCad project?

**Comment by neuralaxy** [comment]
Hello Gaudat,

Thank you for your email and for bringing this to my attention. I have now
uploaded the gerber files on Github:
https://github.com/neuralaxy/NeuroStimDuino/tree/main/Gerbers/Gerbers_v1_1.
Please let me know if you have any issues in accessing the files.

I checked, but it seems that there is no proper way to export a KiCad
compatible project from Eagle. On one forum it was mentioned that KiCad is
able to open the board files (.brd) but not the schematic (.sch) files.
Have you tried this? I don't know how useful it will be, since I haven't
used KiCad before. Let me know if you are able to make this work. Sorry, I
wish I could be more helpful to you in this regard.

**Comment by yanwang631** [comment]
Hi, I am a graduate student researching about functional electrical stimulation control strategy, I reproduced NeuroStimDuino according to your information, but after the soldering is done, the computer does not recognize the port when I connect it via usb. We have troubleshoot some problems but still can't succeed, can you help me to analyze the reason?Can you give me a process of using the equipment？

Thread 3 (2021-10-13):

### ISSUE TITLE
USB port identification

### ISSUE THREAD

**Issue by yanwang631** [neuralaxy/NeuroStimDuino#3]
Hi, I am a graduate student researching about functional electrical stimulation control strategy, I reproduced NeuroStimDuino according to your information, but after the soldering is done, the computer does not recognize the port when I connect it via usb. We have troubleshoot some problems but still can't succeed, can you help me to analyze the reason?Can you give me a process of using the equipment？

**Comment by neuralaxy** [comment]
Hi @yanwang631 
The USB port is controlled by an FTDI USB-to-serial chip (FT232RL). Have you tried installing FTDI drivers?

**Comment by yanwang631** [comment]
Thank you very much for your answer, now I am facing the problem that when I connect to the computer through usb, the computer does not show any port, I checked the power supply of FT232RL and dsp, it is normal, so now I am very confused and would like to ask you what could be the reason for this

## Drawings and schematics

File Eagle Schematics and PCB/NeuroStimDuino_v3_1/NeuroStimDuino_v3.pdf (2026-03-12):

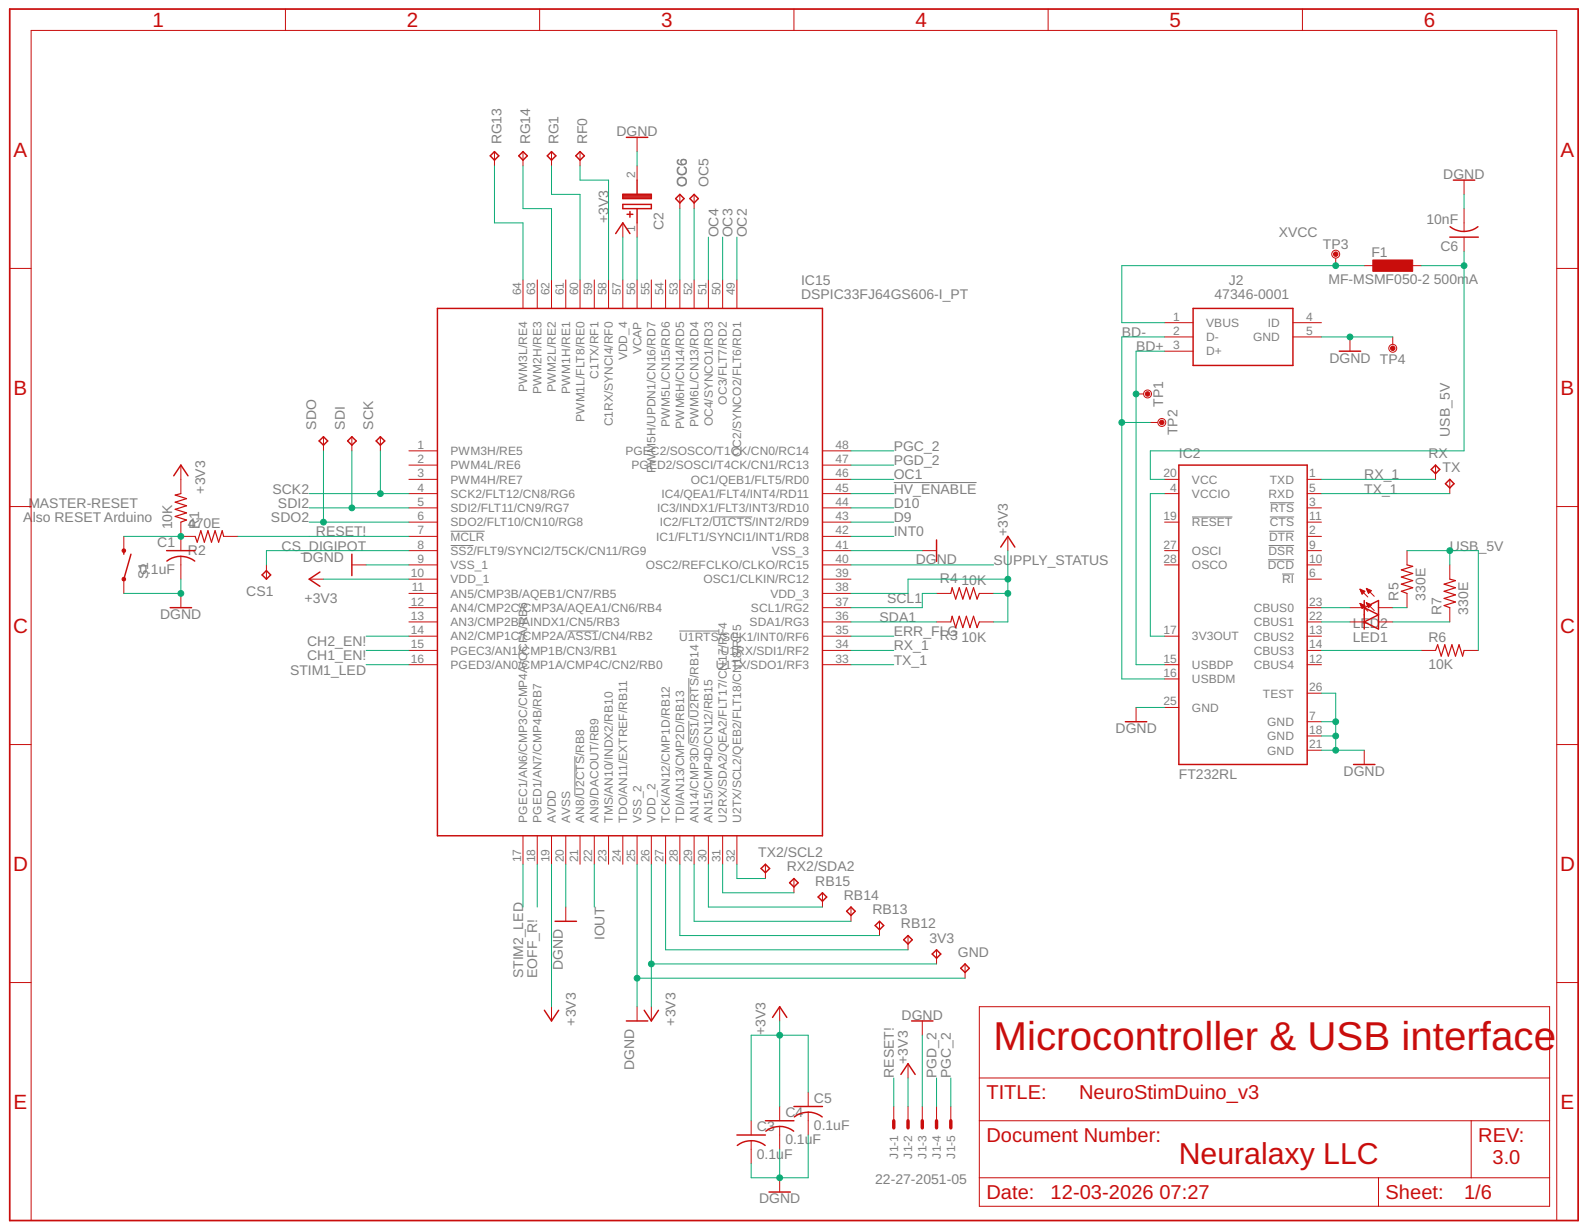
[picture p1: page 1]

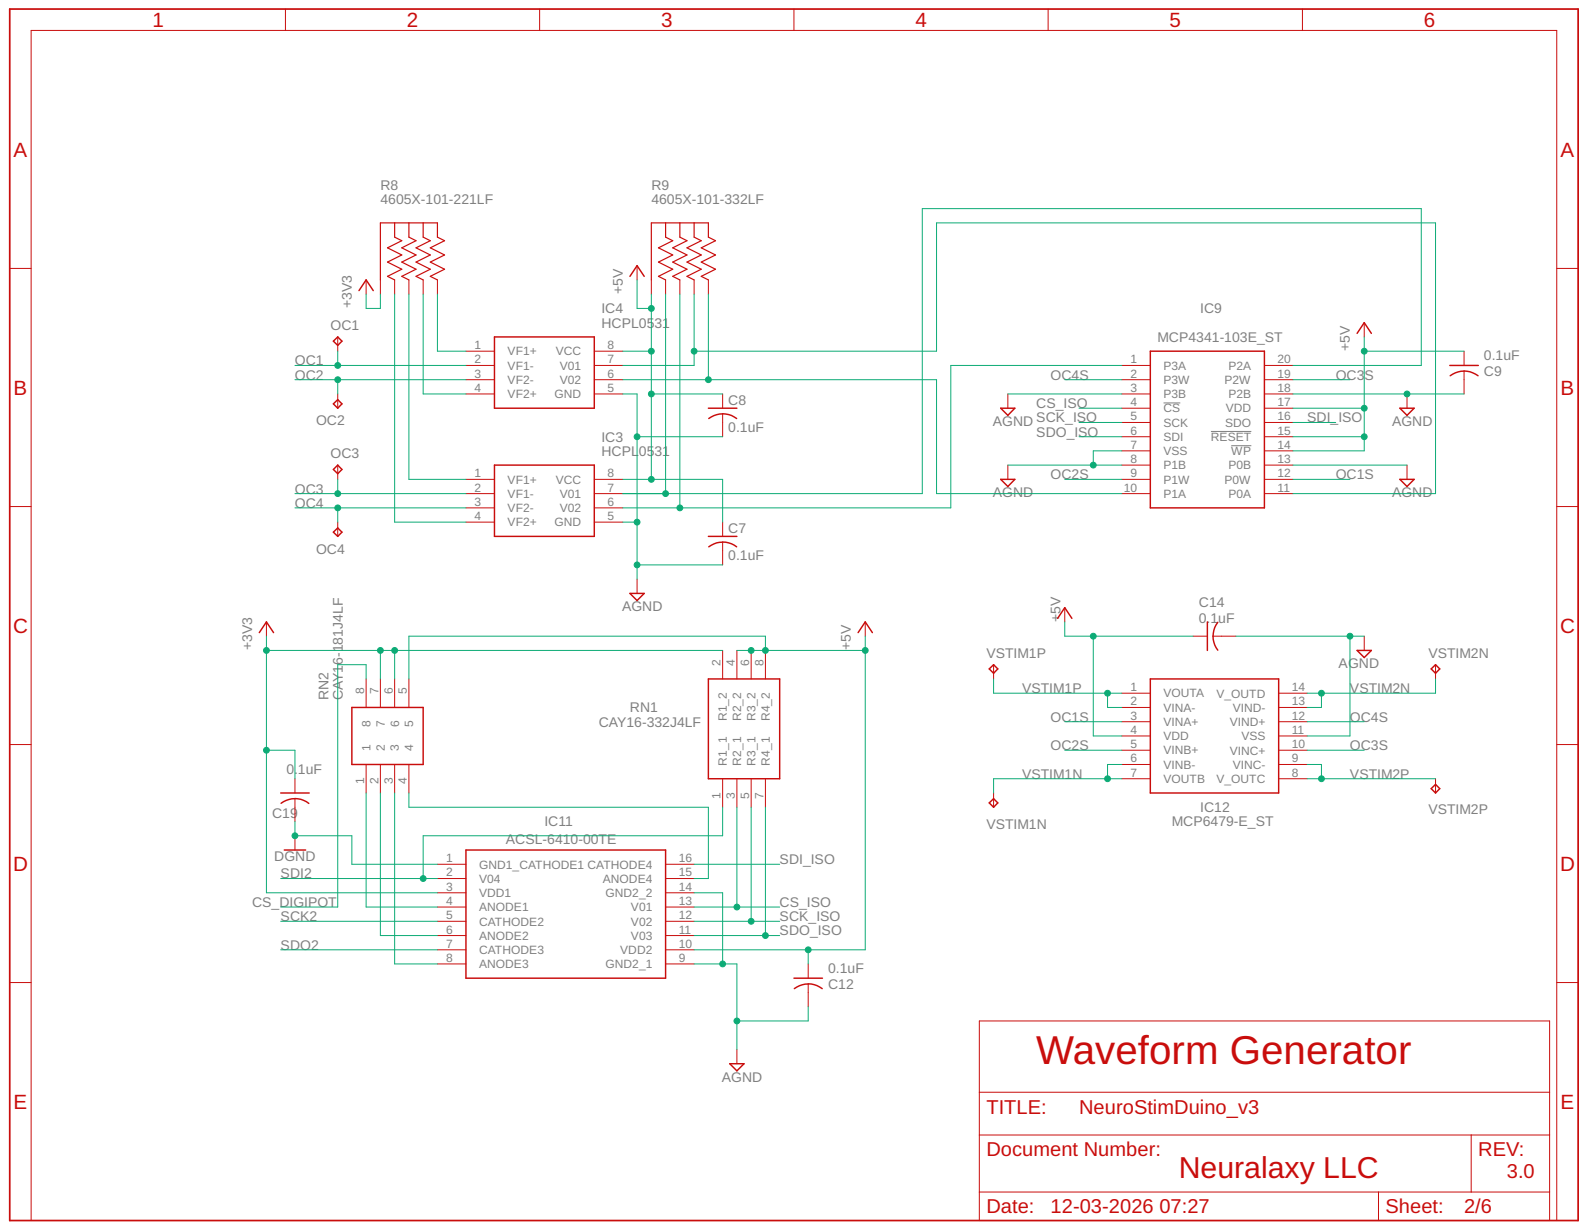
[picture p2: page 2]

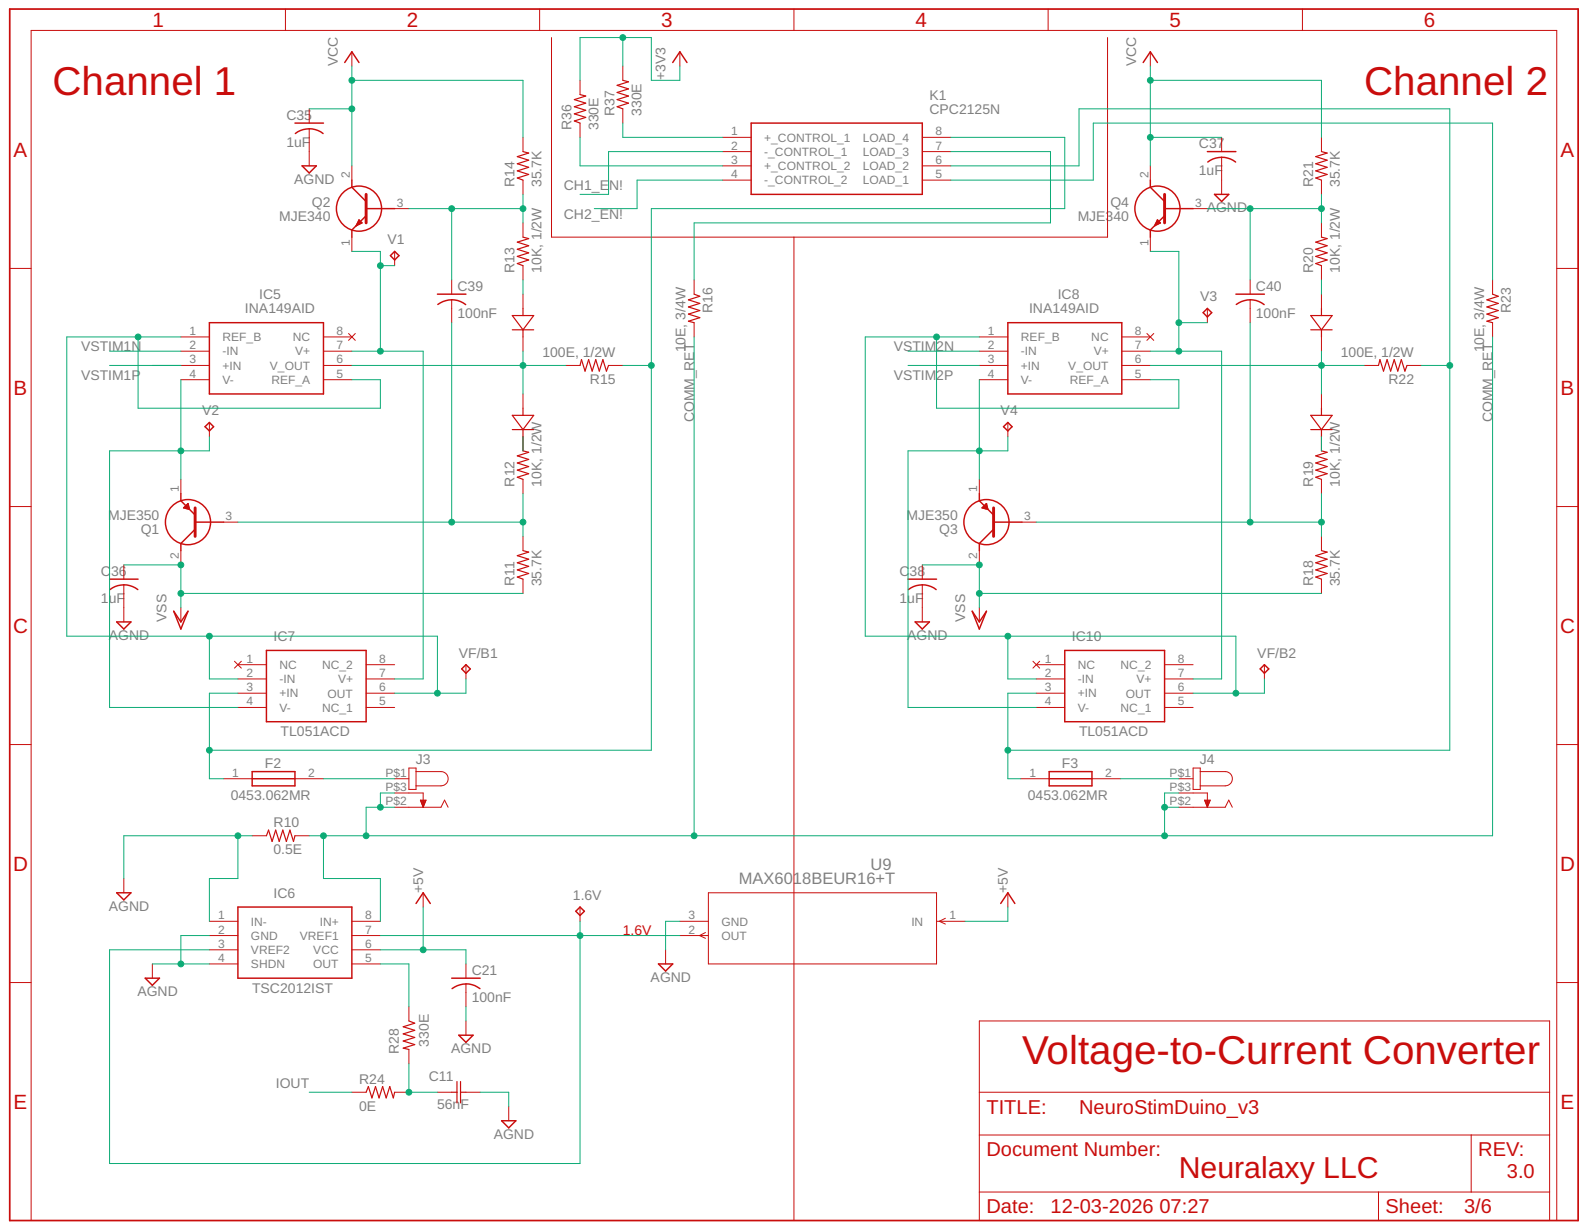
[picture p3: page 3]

Voltage-to-Current Converter

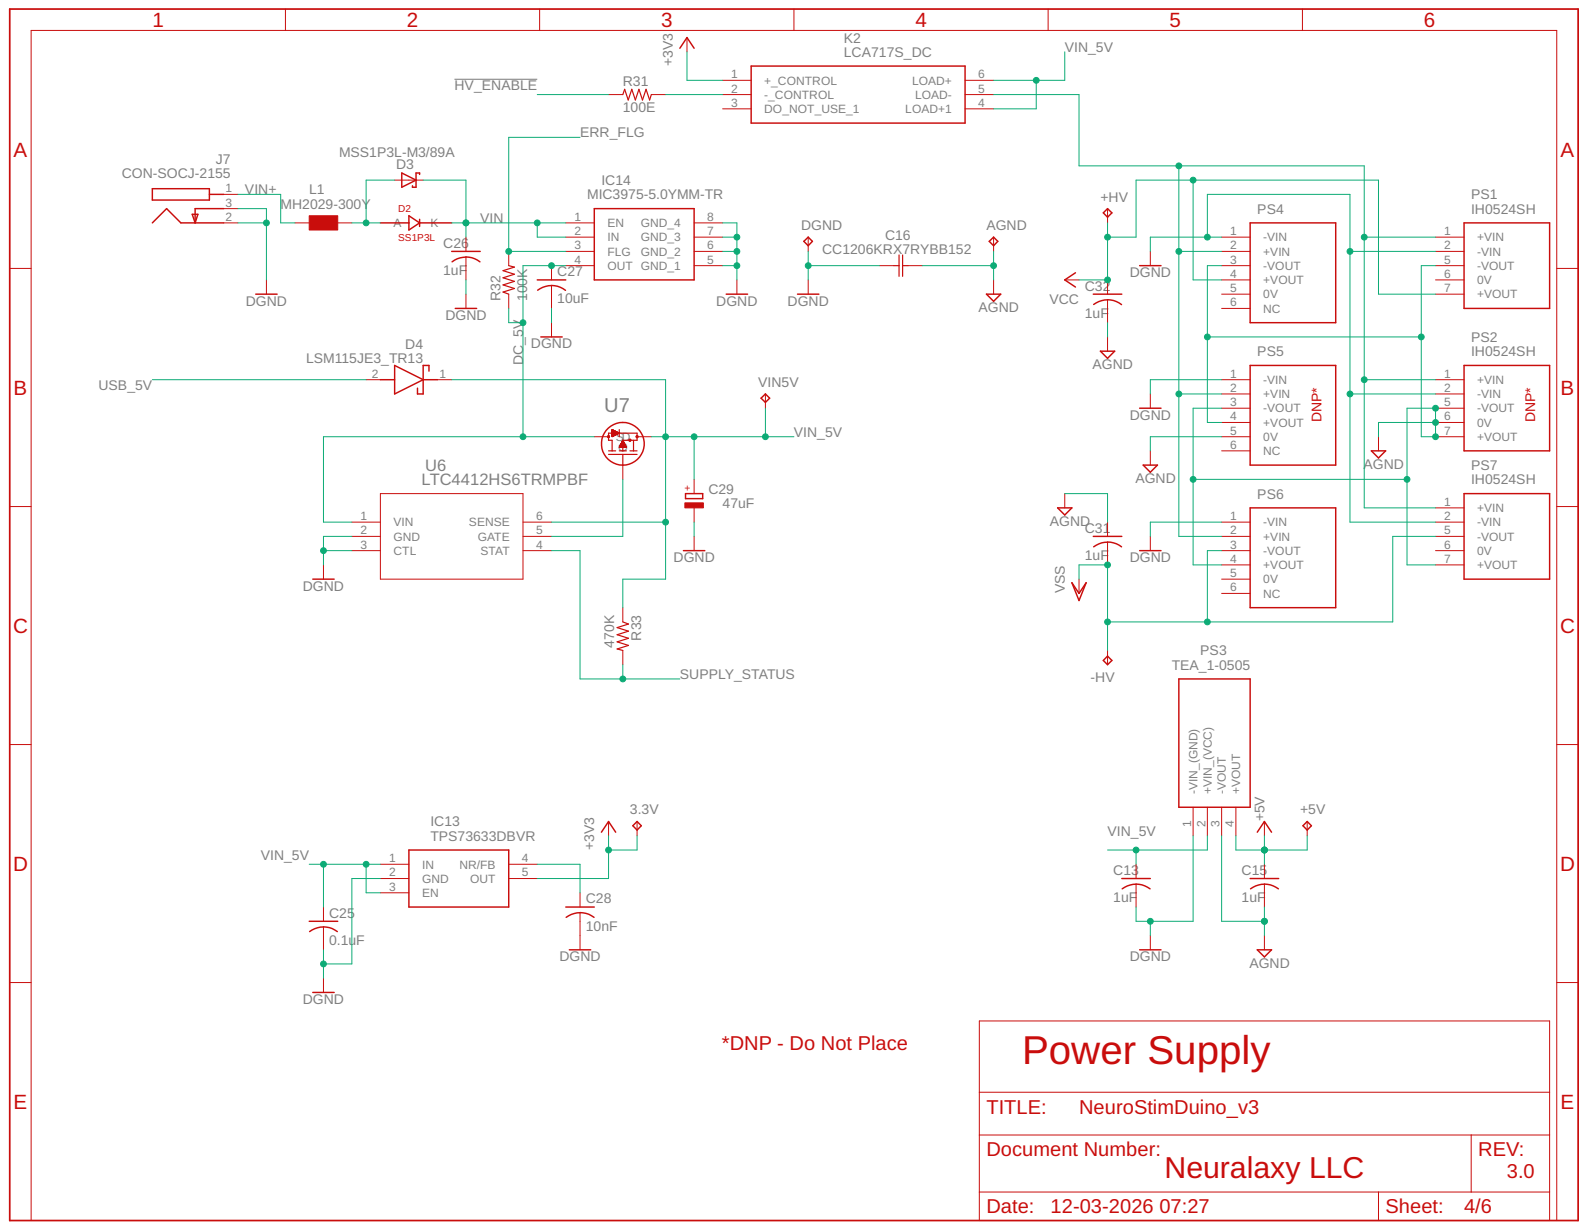
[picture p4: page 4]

*DNP - Do Not Place

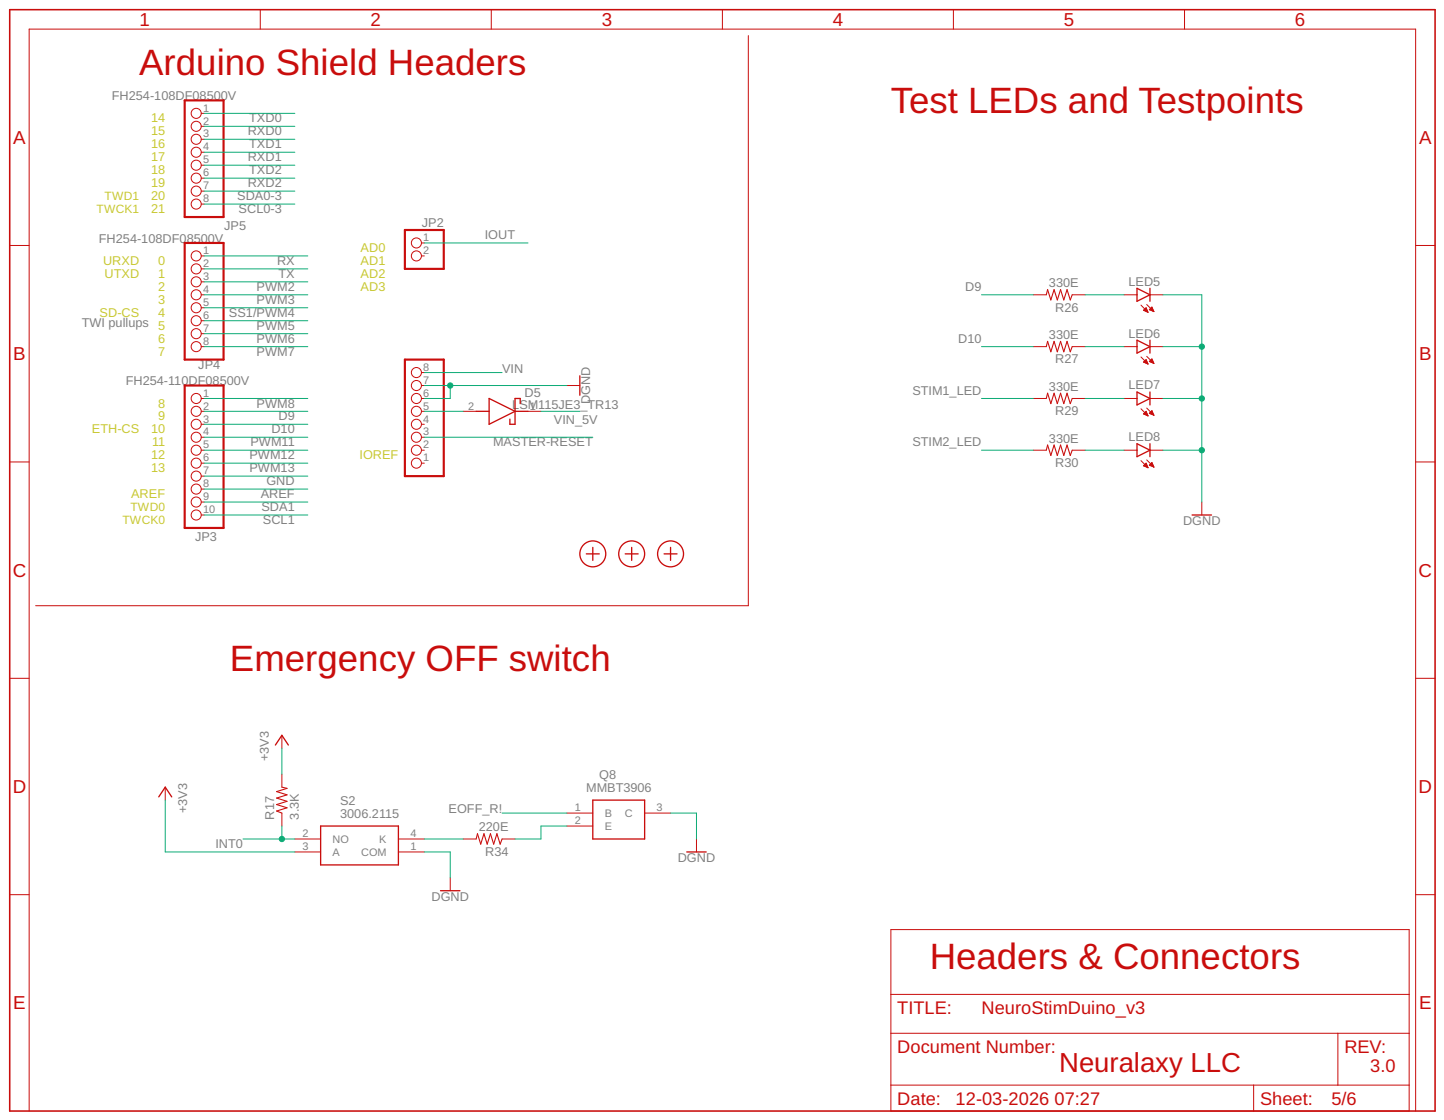
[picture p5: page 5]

Test LEDs and Testpoints

# Revision History

# Revision History (Changes from NeuroStimDuino version 2.1)

# 1. Replaced NMT0572SC (obsolete) with IH0524XX. XX stands for ability to connect both

# IH0524SH or IH0524S

# 2. Replaced manual HV switched with digital Solid-state Relay 3. PS2 and PS5 are redundant and not used. **Their output pins are grounded**

## DISCLAIMER

Reference Designs ARE PROVIDED "AS IS" AND "WITH ALL FAULTS. Neuralaxy LLC DISCLAIMS ALL OTHER WARRANTIES, EXPRESS OR IMPLIED, REGARDING PRODUCTS, INCLUDING BUT NOT LIMITED TO, ANY IMPLIED WARRANTIES OR MERCHANTABILITY OR FITNESS FOR A PARTICULAR PURPOSE

Neuralaxy LLC may make changes to specifications and product descriptions at any time, without notice. The Customer must not rely on the absence or characteristics of any features or instructions marked "reserved" or "undefined". Neuralaxy LLC reserves these for future definition and shall have no responsibility whatsoever for conflicts or incompabilities arising from future changes to them. The product information on the Web Site or Materials is subject to change without

## notice. Do not finalize a design with this info

A

B | B
C | C
D | D

E

A

E

## REV:

## TITLE:

## Document Number:

## NeuroStimDuino_v3

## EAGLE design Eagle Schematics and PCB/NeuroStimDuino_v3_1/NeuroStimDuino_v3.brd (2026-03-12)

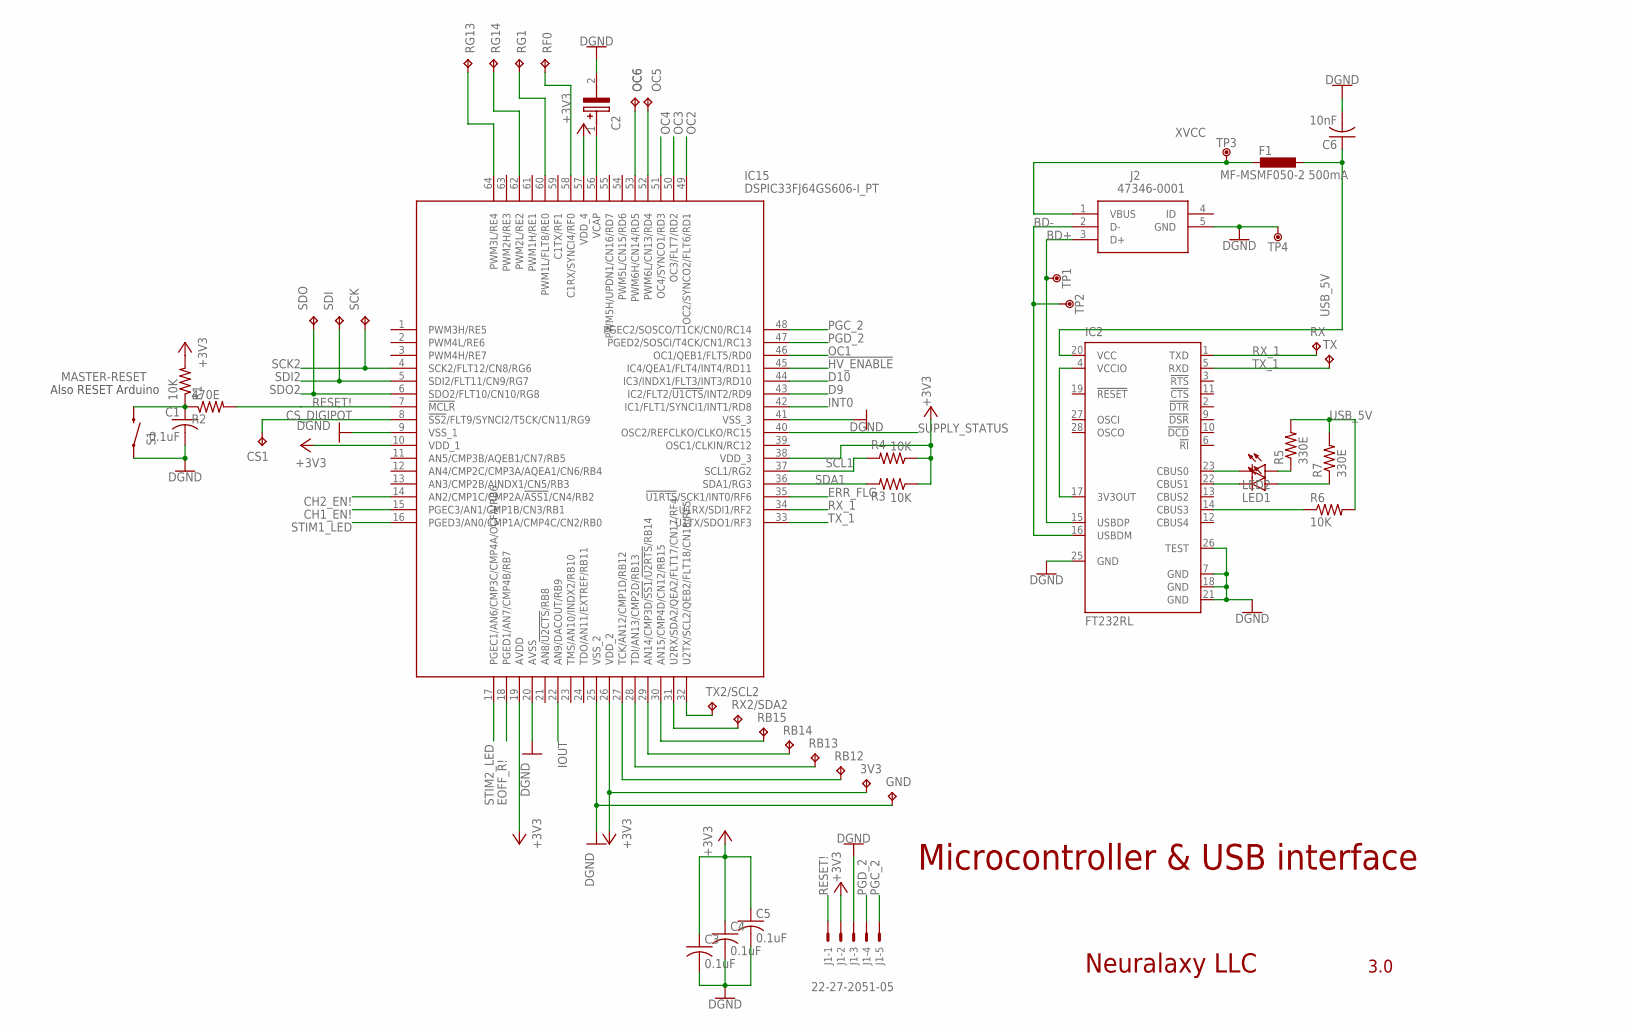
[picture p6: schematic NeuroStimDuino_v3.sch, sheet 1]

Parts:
3V3: TPTP08R; TP08R
/OC5: TPTP08R; TP08R
C1: 0.1uF; C0805
C2: F971C475MAAHT3; CAPPM3216X180N
C3, C4, C5: 0.1uF; C1206
C6: 10nF; C1206
CS1: TPTP08R; TP08R
F1: MF-MSMF050-2 500mA; L1812
GND: TPTP08R; TP08R
IC2: FT232RL; SSOP28
IC15: DSPIC33FJ64GS606-I_PT; QFP50P1200X1200X120-64N
J1: 22-27-2051-05; 6410-05
J2: 47346-0001
LED1, LED2: LEDCHIPLED_1206; CHIPLED_1206
OC6: TPTP08R; TP08R
R1: 10K; R0805
R2: 470E; R0805
R3, R4, R6: 10K; R1206
R5, R7: 330E; R1206
RB12, RB13, RB14, RB15: TPTP08R; TP08R
RF0: TPTP08R; TP08R
RG1, RG13, RG14: TPTP08R; TP08R
RX: TPTP20R; TP20R
RX2/SDA2: TPTP08R; TP08R
S1: SWITCH-MOMENTARY-2SMD; TACTILE_SWITCH_SMD
SCK: TPTP10R; TP10R
SDI: TPTP10R; TP10R
SDO: TPTP10R; TP10R
TP1, TP2, TP3, TP4: DNP; TP-1.00MM
TX: TPTP20R; TP20R
TX2/SCL2: TPTP08R; TP08R

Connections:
!HV_ENABLE: IC15.45 (IC4/QEA1/FLT4/INT4/RD11); also elsewhere on the board
+3V3: 3V3.TP, C3.1, C4.1, C5.1, IC15.10 (VDD_1), IC15.19 (AVDD), IC15.26 (VDD_2), IC15.38 (VDD_3), IC15.57 (VDD_4), J1.2, R1.2, R3.1, R4.1; also elsewhere on the board
BD+: IC2.15 (USBDP), J2.3 (D+), TP1.X
BD-: IC2.16 (USBDM), J2.2 (D-), TP2.X
CH1_EN!: IC15.15 (PGEC3/AN1/CMP1B/CN3/RB1); also elsewhere on the board
CH2_EN!: IC15.14 (AN2/CMP1C/CMP2A/!ASS1!/CN4/RB2); also elsewhere on the board
CS_DIGIPOT: CS1.TP, IC15.8 (!SS2!/FLT9/SYNCI2/T5CK/CN11/RG9); also elsewhere on the board
D9: IC15.43 (IC2/FLT2/!U1CTS!/INT2/RD9); also elsewhere on the board
D10: IC15.44 (IC3/INDX1/FLT3/INT3/RD10); also elsewhere on the board
EOFF_R!: IC15.18 (PGED1/AN7/CMP4B/RB7); also elsewhere on the board
ERR_FLG: IC15.35 (!U1RTS!/SCK1/INT0/RF6); also elsewhere on the board
GND: C1.2, C2.2 (-), C3.2, C4.2, C5.2, C6.2, GND.TP, IC2.7 (GND), IC2.18 (GND), IC2.21 (GND), IC2.25 (GND), IC2.26 (TEST), IC15.9 (VSS_1), IC15.20 (AVSS), IC15.25 (VSS_2), IC15.41 (VSS_3), J1.3, J2.5 (GND), S1.1, TP4.X; also elsewhere on the board
INT0: IC15.42 (IC1/FLT1/SYNCI1/INT1/RD8); also elsewhere on the board
IOUT: IC15.22 (AN9/DACOUT/RB9); also elsewhere on the board
MASTER-RESET: C1.1, R1.1, R2.1, S1.3 (2); also elsewhere on the board
unnamed: C2.1 (+), IC15.56 (VCAP)
unnamed: IC15.32 (U2TX/SCL2/QEB2/FLT18/CN18/RF5), TX2/SCL2.TP
unnamed: IC15.31 (U2RX/SDA2/QEA2/FLT17/CN17/RF4), RX2/SDA2.TP
unnamed: IC15.30 (AN15/CMP4D/CN12/RB15), RB15.TP
unnamed: IC15.29 (AN14/CMP3D/!SS1!/!U2RTS!/RB14), RB14.TP
unnamed: IC15.28 (TDI/AN13/CMP2D/RB13), RB13.TP
unnamed: IC15.27 (TCK/AN12/CMP1D/RB12), RB12.TP
unnamed: IC15.58 (C1RX/SYNCI4/RF0), RF0.TP
unnamed: IC15.60 (PWM1L/FLT8/RE0), RG1.TP
unnamed: IC15.62 (PWM2L/RE2), RG14.TP
unnamed: IC15.64 (PWM3L/RE4), RG13.TP
unnamed: IC2.4 (VCCIO), IC2.17 (3V3OUT)
unnamed: IC2.23 (CBUS0), LED2.C
unnamed: LED2.A, R5.1
unnamed: LED1.A, R7.1
unnamed: IC2.22 (CBUS1), LED1.C
unnamed: IC2.14 (CBUS3), R6.1
OC1: IC15.46 (OC1/QEB1/FLT5/RD0); also elsewhere on the board
OC2: IC15.49 (OC2/SYNCO2/FLT6/RD1); also elsewhere on the board
OC3: IC15.50 (OC3/FLT7/RD2); also elsewhere on the board
OC4: IC15.51 (OC4/SYNCO1/RD3); also elsewhere on the board
OC5: /OC5.TP, IC15.52 (PWM6L/CN13/RD4)
OC6: IC15.53 (PWM6H/CN14/RD5), OC6.TP
PGC_2: IC15.48 (PGEC2/SOSCO/T1CK/CN0/RC14), J1.5
PGD_2: IC15.47 (PGED2/SOSCI/T4CK/CN1/RC13), J1.4
RESET!: IC15.7 (!MCLR), J1.1, R2.2
RX_1: IC2.1 (TXD), IC15.34 (U1RX/SDI1/RF2), RX.TP
SCK2: IC15.4 (SCK2/FLT12/CN8/RG6), SCK.TP; also elsewhere on the board
SCL1: IC15.37 (SCL1/RG2), R4.2; also elsewhere on the board
SDA1: IC15.36 (SDA1/RG3), R3.2; also elsewhere on the board
SDI2: IC15.5 (SDI2/FLT11/CN9/RG7), SDI.TP; also elsewhere on the board
SDO2: IC15.6 (SDO2/FLT10/CN10/RG8), SDO.TP; also elsewhere on the board
STIM1_LED: IC15.16 (PGED3/AN0/CMP1A/CMP4C/CN2/RB0); also elsewhere on the board
STIM2_LED: IC15.17 (PGEC1/AN6/CMP3C/CMP4A/OCFA/RB6); also elsewhere on the board
SUPPLY_STATUS: IC15.40 (OSC2/REFCLKO/CLKO/RC15); also elsewhere on the board
TX_1: IC2.5 (RXD), IC15.33 (U1TX/SDO1/RF3), TX.TP
USB_5V: C6.1, F1.1, IC2.20 (VCC), R5.2, R6.2, R7.2; also elsewhere on the board
XVCC: F1.2, J2.1 (VBUS), TP3.X

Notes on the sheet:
Microcontroller & USB interface
Also RESET Arduino
3.0
Neuralaxy LLC

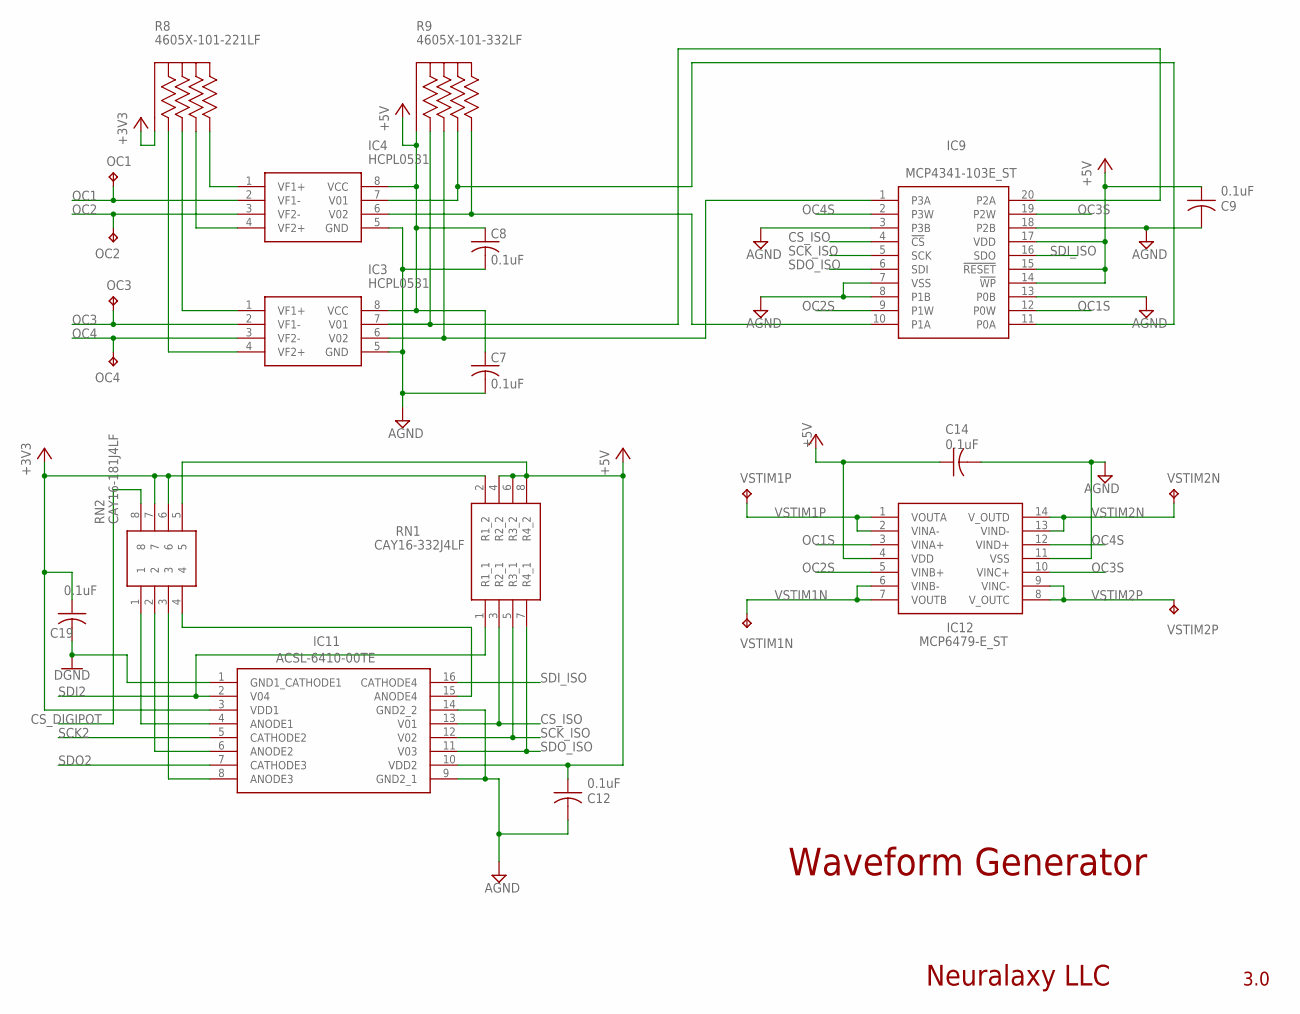
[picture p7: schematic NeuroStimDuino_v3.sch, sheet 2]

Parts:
C7, C8, C9, C12, C14, C19: 0.1uF; C1206
IC3, IC4: HCPL0531; SOIC127P594X363-8N
IC9: MCP4341-103E_ST; SOP65P640X120-20N
IC11: ACSL-6410-00TE; SOIC127P599X152-16N
IC12: MCP6479-E_ST; SOP65P640X120-14N
OC1, OC2: TPTP08R; TP08R
OC3, OC4: TPTP10R; TP10R
R8: 4605X-101-221LF; BO_4605X
R9: 4605X-101-332LF; BO_4605X
RN1: CAY16-332J4LF; CAY16-J4
RN2: CAY16-181J4LF; CAY16181J4LF
VSTIM1N, VSTIM1P, VSTIM2N, VSTIM2P: TPTP08R; TP08R

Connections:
+3V3: C19.1, IC11.3 (VDD1), R8.1, RN1.2 (R1_2), RN2.6, RN2.7; also elsewhere on the board
+5V: C7.1, C8.1, C9.1, C12.1, C14.1, IC3.8 (VCC), IC4.8 (VCC), IC9.14 (!WP), IC9.15 (!RESET), IC9.17 (VDD), IC11.10 (VDD2), IC12.4 (VDD), R9.1, RN1.4 (R2_2), RN1.6 (R3_2), RN1.8 (R4_2), RN2.5; also elsewhere on the board
AGND: C7.2, C8.2, C9.2, C12.2, C14.2, IC3.5 (GND), IC4.5 (GND), IC9.3 (P3B), IC9.7 (VSS), IC9.8 (P1B), IC9.13 (P0B), IC9.18 (P2B), IC11.9 (GND2_1), IC11.14 (GND2_2), IC12.11 (VSS); also elsewhere on the board
CS_DIGIPOT: RN2.8; also elsewhere on the board
CS_ISO: IC9.4 (!CS), IC11.13 (V01), RN1.3 (R2_1)
GND: C19.2, IC11.1 (GND1_CATHODE1); also elsewhere on the board
unnamed: IC11.4 (ANODE1), RN2.1
unnamed: IC4.7 (V01), IC9.11 (P0A), R9.4
unnamed: IC4.6 (V02), IC9.10 (P1A), R9.5
unnamed: IC3.7 (V01), IC9.20 (P2A), R9.2
unnamed: IC3.6 (V02), IC9.1 (P3A), R9.3
unnamed: IC4.4 (VF2+), R8.4
unnamed: IC4.1 (VF1+), R8.5
unnamed: IC3.1 (VF1+), R8.3
unnamed: IC3.4 (VF2+), R8.2
unnamed: IC11.6 (ANODE2), RN2.2
unnamed: IC11.8 (ANODE3), RN2.3
unnamed: IC11.15 (ANODE4), RN2.4
OC1: IC4.2 (VF1-), OC1.TP; also elsewhere on the board
OC1S: IC9.12 (P0W), IC12.3 (VINA+)
OC2: IC4.3 (VF2-), OC2.TP; also elsewhere on the board
OC2S: IC9.9 (P1W), IC12.5 (VINB+)
OC3: IC3.2 (VF1-), OC3.TP; also elsewhere on the board
OC3S: IC9.19 (P2W), IC12.10 (VINC+)
OC4: IC3.3 (VF2-), OC4.TP; also elsewhere on the board
OC4S: IC9.2 (P3W), IC12.12 (VIND+)
SCK2: IC11.5 (CATHODE2); also elsewhere on the board
SCK_ISO: IC9.5 (SCK), IC11.12 (V02), RN1.5 (R3_1)
SDI2: IC11.2 (V04), RN1.1 (R1_1); also elsewhere on the board
SDI_ISO: IC9.16 (SDO), IC11.16 (CATHODE4)
SDO2: IC11.7 (CATHODE3); also elsewhere on the board
SDO_ISO: IC9.6 (SDI), IC11.11 (V03), RN1.7 (R4_1)
VSTIM1N: IC12.6 (VINB-), IC12.7 (VOUTB), VSTIM1N.TP; also elsewhere on the board
VSTIM1P: IC12.1 (VOUTA), IC12.2 (VINA-), VSTIM1P.TP; also elsewhere on the board
VSTIM2N: IC12.13 (VIND-), IC12.14 (V_OUTD), VSTIM2N.TP; also elsewhere on the board
VSTIM2P: IC12.8 (V_OUTC), IC12.9 (VINC-), VSTIM2P.TP; also elsewhere on the board

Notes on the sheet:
Waveform Generator
Neuralaxy LLC
3.0

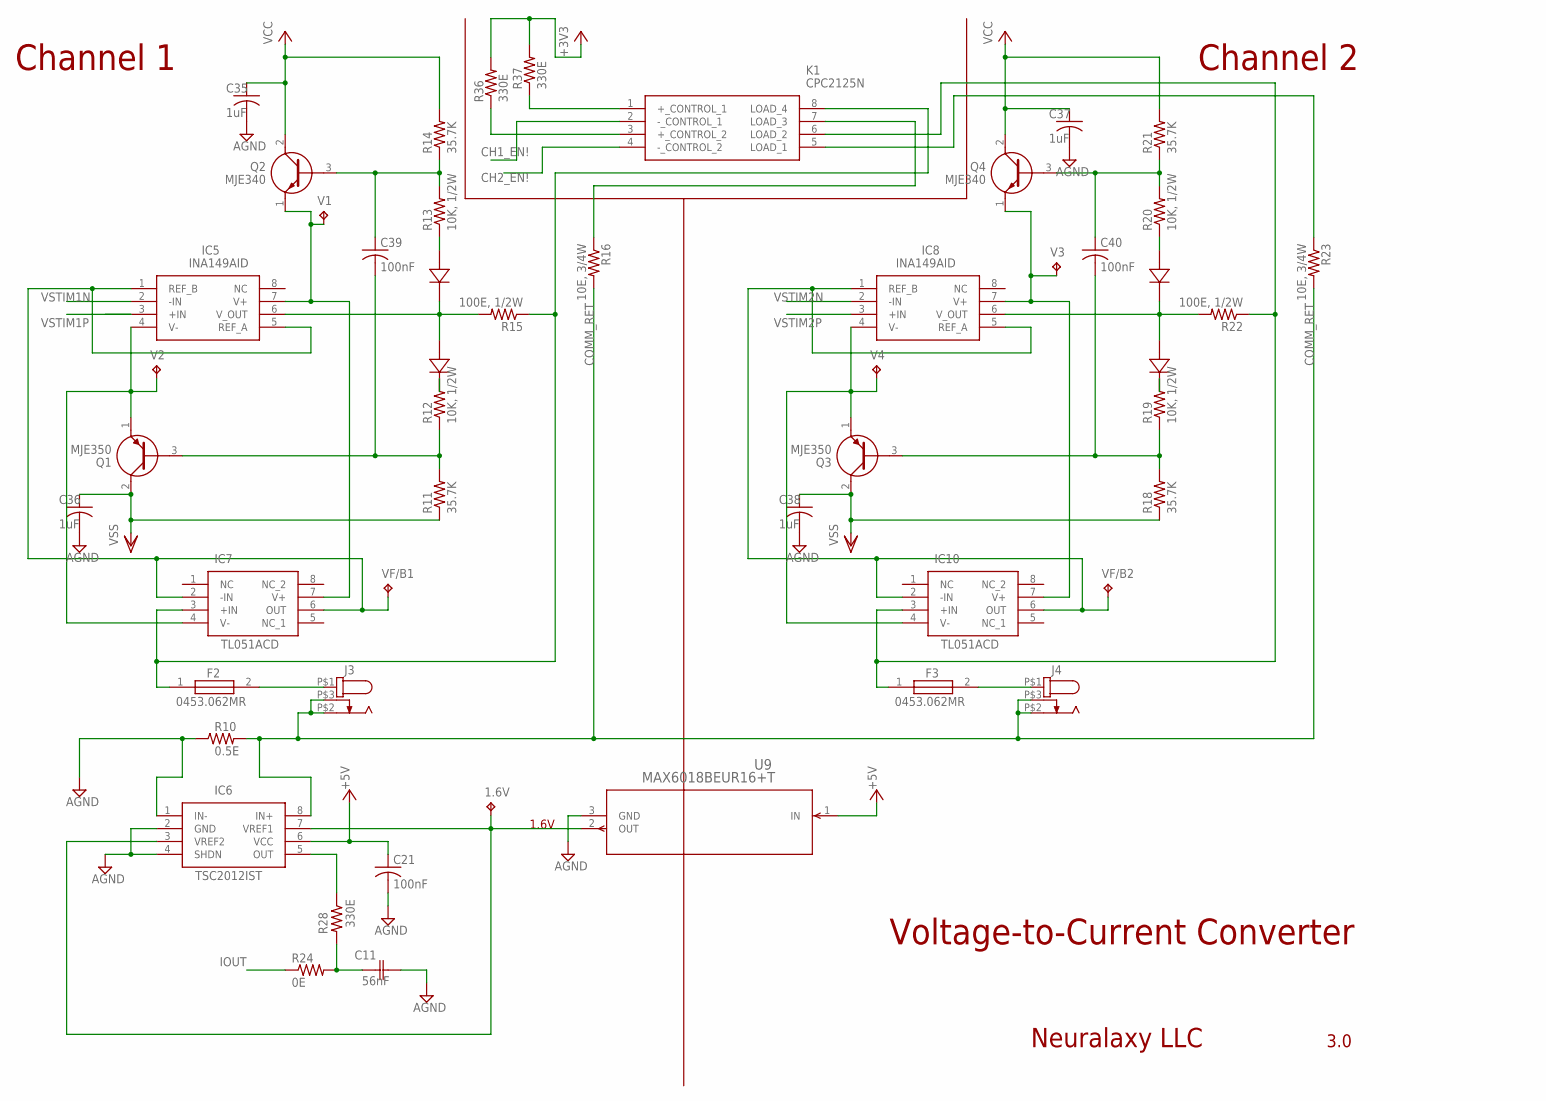
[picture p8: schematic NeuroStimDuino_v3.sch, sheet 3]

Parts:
1.6V: TPTP10R; TP10R
C11: 56nF; CAPC17595_87N_KEM
C21: 100nF; C1206
C35, C36, C37, C38: 1uF; C0805
C39, C40: 100nF; C0805K
D6, D7, D8, D9: GF1J-E3DO-214BA-L; DO-214BA-L
F2, F3: 0453.062MR; FUSC6127X294N
IC5, IC8: INA149AID; SOIC127P600X175-8N
IC6: TSC2012IST; SOP65P490X110-8N
IC7, IC10: OPA140AID; SOIC127P600X175-8N
J3, J4: DC_JACK_081BB-2103300; 081BB-2103300
K1: CPC2125N; SOP254P610X218-8N
Q1, Q3: MJE350; TO229P300X760X1364-3P
Q2, Q4: MJE340; TO229P290X760X1320-3P
R10: 0.5E; R1206
R11, R14, R18, R21: 35.7K; R1206
R12, R13, R19, R20: 10K, 1/2W; R1206
R15, R22: 100E, 1/2W; R1206
R16, R23: 10E, 3/4W; R1206
R24: 0E; R1206
R28: 330E; R0603
R36, R37: 330E; R1206
U9: MAX6018BEUR16+T; 21-0051H_MXM
V1, V2, V3, V4: TPTP10R; TP10R
VF/B1, VF/B2: TPTP10R; TP10R

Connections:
+3V3: R36.2, R37.2; also elsewhere on the board
+5V: C21.1, IC6.6 (VCC), U9.1 (IN); also elsewhere on the board
AGND: C11.2, C21.2, C35.2, C36.2, C37.2, C38.2, IC6.1 (IN-), IC6.2 (GND), IC6.4 (SHDN), R10.1, U9.3 (GND); also elsewhere on the board
CH1_EN!: K1.2 (-_CONTROL_1); also elsewhere on the board
CH2_EN!: K1.4 (-_CONTROL_2); also elsewhere on the board
COMM_RET: IC6.8 (IN+), J3.P$2 (2), J3.P$3 (3), J4.P$2 (2), J4.P$3 (3), R10.2, R16.2, R23.2
IOUT: R24.1; also elsewhere on the board
unnamed: K1.1 (+_CONTROL_1), R37.1
unnamed: K1.3 (+_CONTROL_2), R36.1
unnamed: IC6.5 (OUT), R28.1
unnamed: 1.6V.TP, IC6.3 (VREF2), IC6.7 (VREF1), U9.2 (OUT)
unnamed: C11.1, R24.2, R28.2
unnamed: IC5.4 (V-), IC7.4 (V-), Q1.1 (E), V2.TP
unnamed: IC5.1 (REF_B), IC5.5 (REF_A), IC7.2 (-IN), IC7.6 (OUT), VF/B1.TP
unnamed: C39.1, Q2.3 (B), R13.2, R14.1
unnamed: C39.2, Q1.3 (B), R11.2, R12.1
unnamed: D6.2, R13.1
unnamed: D7.1, R12.2
unnamed: D6.1, D7.2, IC5.6 (V_OUT), R15.2
unnamed: IC5.7 (V+), IC7.7 (V+), Q2.1 (E), V1.TP
unnamed: K1.7 (LOAD_3), R16.1
unnamed: F2.1, IC7.3 (+IN), K1.8 (LOAD_4), R15.1
unnamed: K1.5 (LOAD_1), R23.1
unnamed: F2.2, J3.P$1 (1)
unnamed: C40.1, Q4.3 (B), R20.2, R21.1
unnamed: C40.2, Q3.3 (B), R18.2, R19.1
unnamed: D8.2, R20.1
unnamed: D9.1, R19.2
unnamed: D8.1, D9.2, IC8.6 (V_OUT), R22.2
unnamed: IC8.1 (REF_B), IC8.5 (REF_A), IC10.2 (-IN), IC10.6 (OUT), VF/B2.TP
unnamed: IC8.7 (V+), IC10.7 (V+), Q4.1 (E), V3.TP
unnamed: IC8.4 (V-), IC10.4 (V-), Q3.1 (E), V4.TP
unnamed: F3.1, IC10.3 (+IN), K1.6 (LOAD_2), R22.1
unnamed: F3.2, J4.P$1 (1)
VCC: C35.1, C37.1, Q2.2 (C), Q4.2 (C), R14.2, R21.2; also elsewhere on the board
VSS: C36.1, C38.1, Q1.2 (C), Q3.2 (C), R11.1, R18.1; also elsewhere on the board
VSTIM1N: IC5.2 (-IN); also elsewhere on the board
VSTIM1P: IC5.3 (+IN); also elsewhere on the board
VSTIM2N: IC8.2 (-IN); also elsewhere on the board
VSTIM2P: IC8.3 (+IN); also elsewhere on the board

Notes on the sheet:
Voltage-to-Current Converter
Channel 1
Channel 2
1.6V
TSC2012IST
Neuralaxy LLC
3.0
TL051ACD

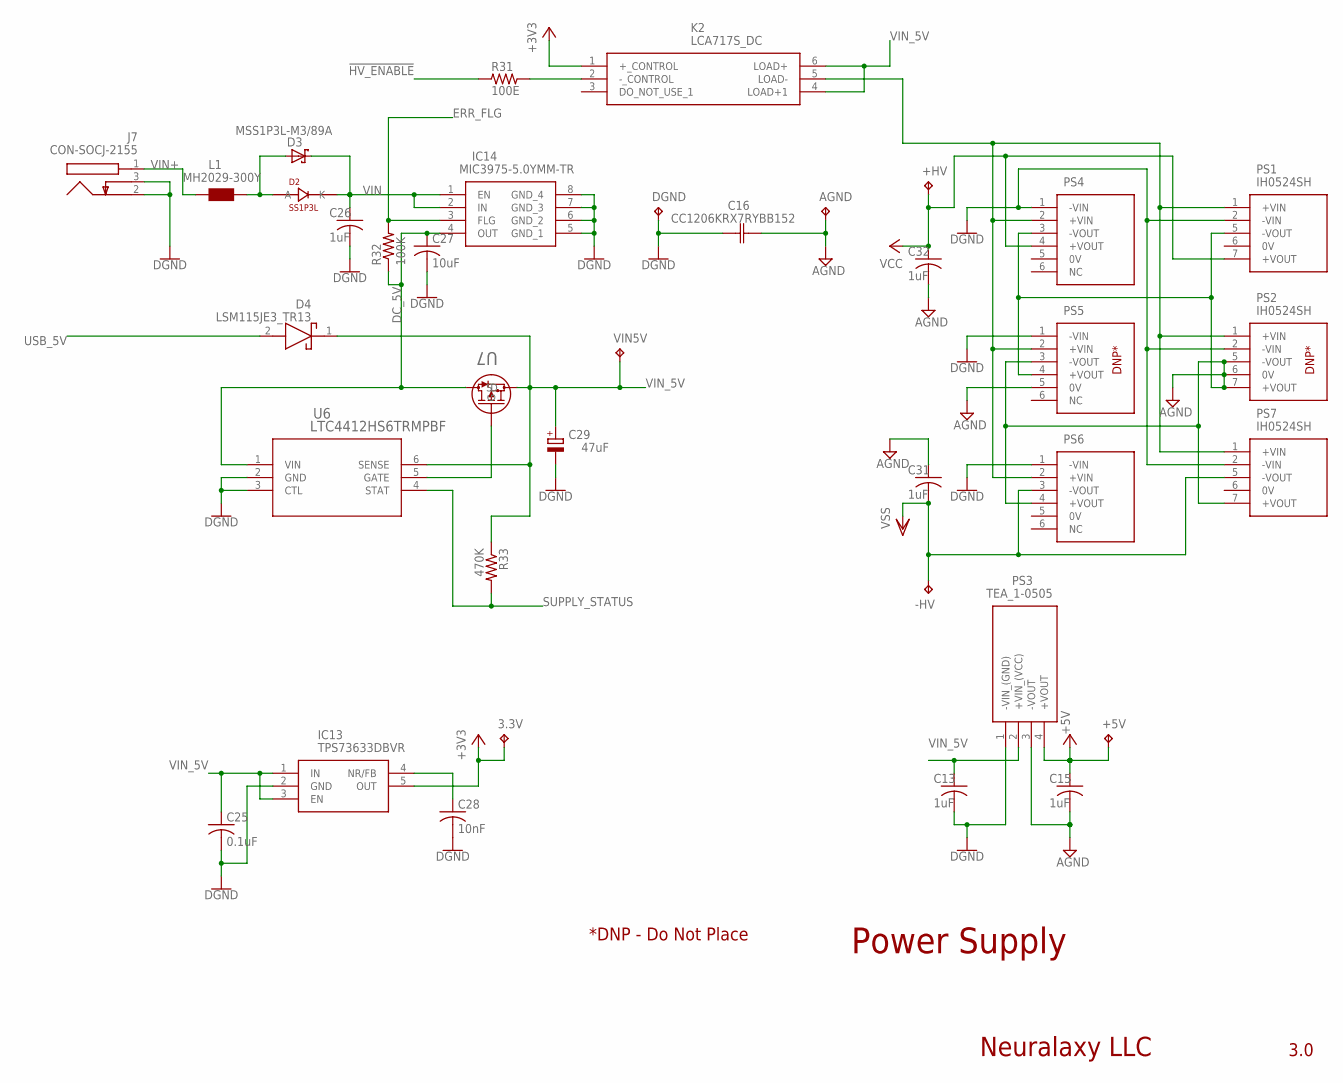
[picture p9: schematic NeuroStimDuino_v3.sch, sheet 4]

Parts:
3.3V: TPTP10R; TP10R
+5V: TPTP10R; TP10R
+HV: TPTP10R; TP10R
-HV: TPTP10R; TP10R
AGND: TPTP10R; TP10R
C13, C15, C26, C31, C32: 1uF; C0805
C16: CC1206KRX7RYBB152; CAP_CC1206_YAG
C25: 0.1uF; C1206
C27: 10uF; C0805
C28: 10nF; C1206
C29: 47uF; PANASONIC_D
D2: SS1P3L; DO220AAL
D3: MSS1P3L-M3/89A; MICROSMP
D4: LSM115JE3_TR13; DIOM5436X330N
DGND: TPTP10R; TP10R
IC13: TPS73633DBVR; SOT95P280X145-5N
IC14: MIC3975-5.0YMM-TR; SOP65P490X109-8N
J7: CON-SOCJ-2155; CONSOCJ2155
K2: LCA717S_DC; SOP254P952X470-6N
L1: MH2029-300Y; 0805
PS1, PS2, PS7: IH0524SH
PS3: TEA_1-0505; TEA10505
PS4, PS5, PS6: IH0524D
R31: 100E; R0805
R32: 100K; R1206
R33: 470K; R1206
U6: LTC4412HS6TRMPBF; TSOT-23_S6_ADI
U7: PMV48XP,215TO-236_SOT23_NEX-L; TO-236_SOT23_NEX-L
VIN5V: TPTP10R; TP10R

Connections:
!HV_ENABLE: R31.1; also elsewhere on the board
+3V3: 3.3V.TP, IC13.5 (OUT), K2.1 (+_CONTROL); also elsewhere on the board
+5V: +5V.TP, C15.1, PS3.4 (+VOUT); also elsewhere on the board
AGND: AGND.TP, C15.2, C16.2, C31.1, C32.2, PS1.5 (-VOUT), PS2.5 (-VOUT), PS2.6 (0V), PS2.7 (+VOUT), PS3.3 (-VOUT), PS4.3 (-VOUT), PS5.3 (-VOUT), PS5.4 (+VOUT), PS5.5 (0V), PS6.4 (+VOUT), PS7.7 (+VOUT); also elsewhere on the board
DC_5V: C27.1, IC14.4 (OUT), R32.1, U6.1 (VIN), U7.3 (D)
ERR_FLG: IC14.3 (FLG), R32.2; also elsewhere on the board
GND: C13.2, C16.1, C25.2, C26.2, C27.2, C28.2, C29.-, DGND.TP, IC13.2 (GND), IC14.5 (GND_1), IC14.6 (GND_2), IC14.7 (GND_3), IC14.8 (GND_4), J7.2, J7.3, PS1.2 (-VIN), PS2.2 (-VIN), PS3.1 (-VIN_(GND)), PS4.1 (-VIN), PS5.1 (-VIN), PS6.1 (-VIN), PS7.2 (-VIN), U6.2 (GND), U6.3 (CTL); also elsewhere on the board
unnamed: C28.1, IC13.4 (NR/FB)
unnamed: K2.5 (LOAD-), PS1.1 (+VIN), PS2.1 (+VIN), PS4.2 (+VIN), PS5.2 (+VIN), PS6.2 (+VIN), PS7.1 (+VIN)
unnamed: U6.5 (GATE), U7.1 (G)
unnamed: K2.2 (-_CONTROL), R31.2
unnamed: D2.P$2 (A), D3.A, L1.1
SUPPLY_STATUS: R33.2, U6.4 (STAT); also elsewhere on the board
USB_5V: D4.2 (A); also elsewhere on the board
VCC: +HV.TP, C32.1, PS1.7 (+VOUT), PS4.4 (+VOUT); also elsewhere on the board
VIN: C26.1, D2.P$1 (K), D3.K (C), IC14.1 (EN), IC14.2 (IN); also elsewhere on the board
VIN+: J7.1, L1.2
VIN_5V: C13.1, C25.1, C29.+, D4.1 (K), IC13.1 (IN), IC13.3 (EN), K2.4 (LOAD+1), K2.6 (LOAD+), PS3.2 (+VIN_(VCC)), R33.1, U6.6 (SENSE), U7.2 (S), VIN5V.TP; also elsewhere on the board
VSS: -HV.TP, C31.2, PS6.3 (-VOUT), PS7.5 (-VOUT); also elsewhere on the board

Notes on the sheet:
Power Supply
Neuralaxy LLC
3.0
DNP*
*DNP - Do Not Place

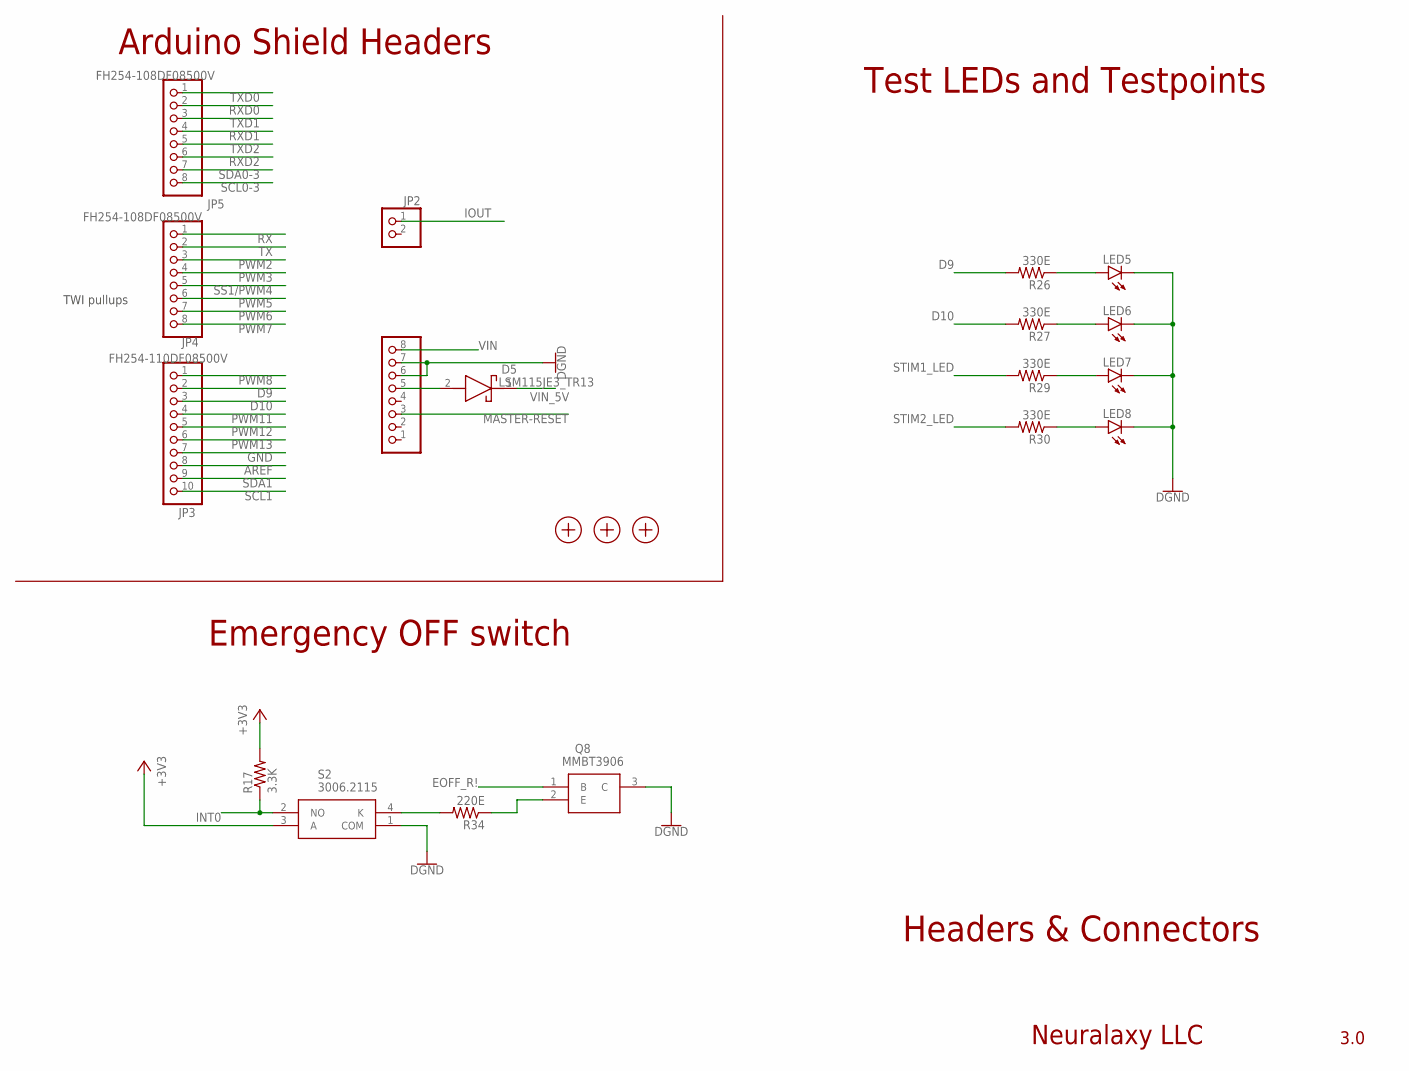
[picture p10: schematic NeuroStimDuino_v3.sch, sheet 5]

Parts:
D5: LSM115JE3_TR13; DIOM5436X330N
JP2: PINHD-1X2; 1X02
JP3: FH254-110DF08500V; 1X10
JP4, JP5, JP6: FH254-108DF08500V; 1X08
LED5, LED6, LED7, LED8: LEDCHIPLED_1206; CHIPLED_1206
Q8: MMBT3906; SOT95P240X120-3N
R17: 3.3K; R1206
R26, R27, R29, R30: 330E; R0603
R34: 220E; R1206
S2: 3006.2115; 30062115
U$1, U$2, U$3: FIDUCIALMOUNT; FIDUCIA-MOUNT

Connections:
+3V3: R17.2, S2.3 (A); also elsewhere on the board
AREF: JP3.8
D9: JP3.2, R26.2; also elsewhere on the board
D10: JP3.3, R27.2; also elsewhere on the board
EOFF_R!: Q8.1 (B); also elsewhere on the board
GND: JP3.7, JP6.6, JP6.7, LED5.C, LED6.C, LED7.C, LED8.C, Q8.3 (C), S2.1 (COM); also elsewhere on the board
INT0: R17.1, S2.2 (NO); also elsewhere on the board
IOUT: JP2.1; also elsewhere on the board
MASTER-RESET: JP6.3; also elsewhere on the board
unnamed: D5.2 (A), JP6.5
unnamed: R34.2, S2.4 (K)
unnamed: Q8.2 (E), R34.1
unnamed: LED8.A, R30.1
unnamed: LED7.A, R29.1
unnamed: LED6.A, R27.1
unnamed: LED5.A, R26.1
PWM2: JP4.3
PWM3: JP4.4
PWM5: JP4.6
PWM6: JP4.7
PWM7: JP4.8
PWM8: JP3.1
PWM11: JP3.4
PWM12: JP3.5
PWM13: JP3.6
RX: JP4.1
RXD0: JP5.2
RXD1: JP5.4
RXD2: JP5.6
SCL0-3: JP5.8
SCL1: JP3.10; also elsewhere on the board
SDA0-3: JP5.7
SDA1: JP3.9; also elsewhere on the board
SS1/PWM4: JP4.5
STIM1_LED: R29.2; also elsewhere on the board
STIM2_LED: R30.2; also elsewhere on the board
TX: JP4.2
TXD0: JP5.1
TXD1: JP5.3
TXD2: JP5.5
VIN: JP6.8; also elsewhere on the board
VIN_5V: D5.1 (K); also elsewhere on the board

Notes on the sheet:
Headers & Connectors
TWI pullups
Arduino Shield Headers
Test LEDs and Testpoints
Emergency OFF switch
Neuralaxy LLC
3.0

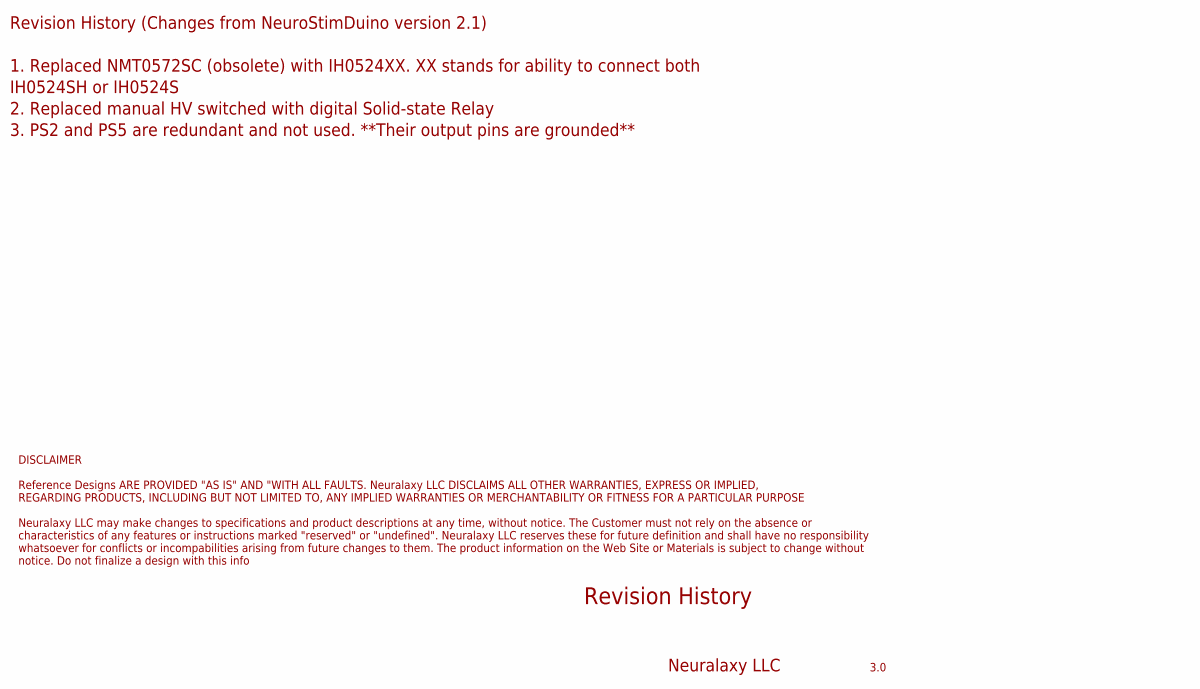
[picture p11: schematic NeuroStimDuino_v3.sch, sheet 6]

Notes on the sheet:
Revision History
Revision History (Changes from NeuroStimDuino version 2.1) 1. Replaced NMT0572SC (obsolete) with IH0524XX. XX stands for ability to connect both IH0524SH or IH0524S 2. Replaced manual HV switched with digital Solid-state Relay 3. PS2 and PS5 are redundant and not used. **Their output pins are groun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
DISCLAIMER Reference Designs ARE PROVIDED "AS IS" AND "WITH ALL FAULTS. Neuralaxy LLC DISCLAIMS ALL OTHER WARRANTIES, EXPRESS OR IMPLIED, REGARDING PRODUCTS, INCLUDING BUT NOT LIMITED TO, ANY IMPLIED WARRANTIES OR MERCHANTABILITY OR FITNESS FOR A PARTICULAR PURPOSE Neuralaxy LLC may make changes to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
Neuralaxy LLC
3.0

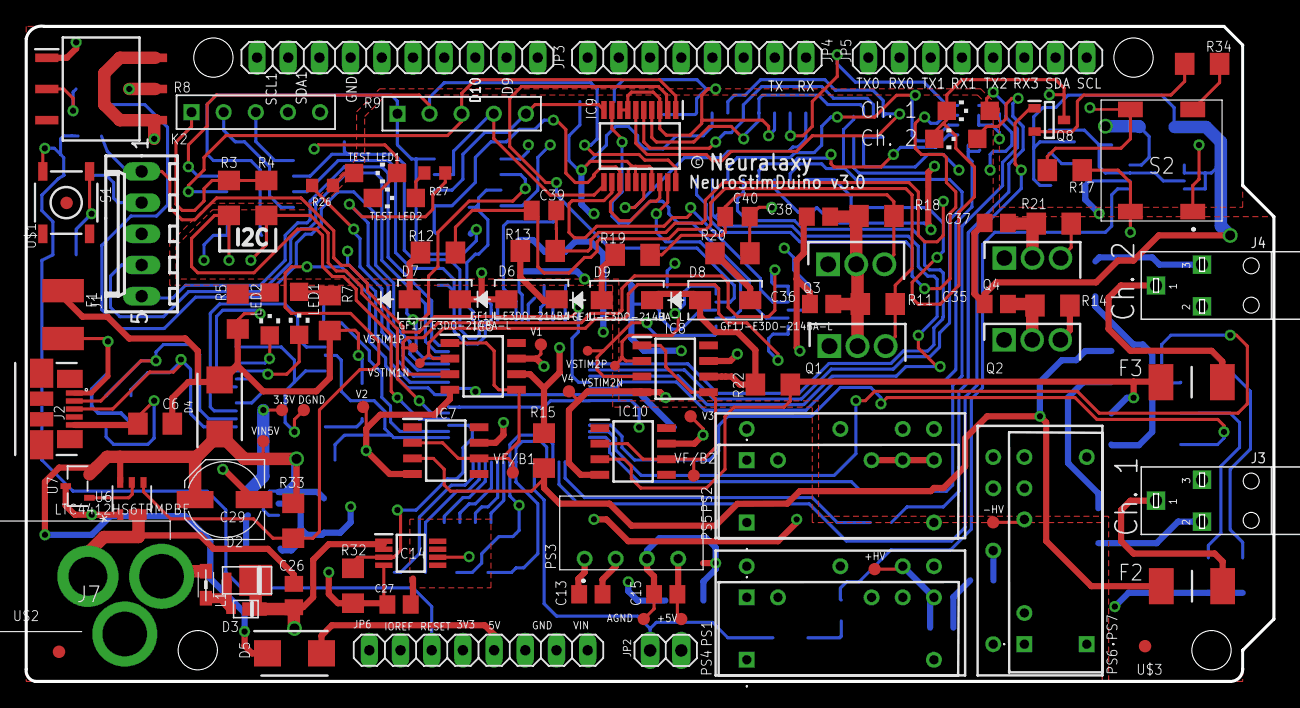
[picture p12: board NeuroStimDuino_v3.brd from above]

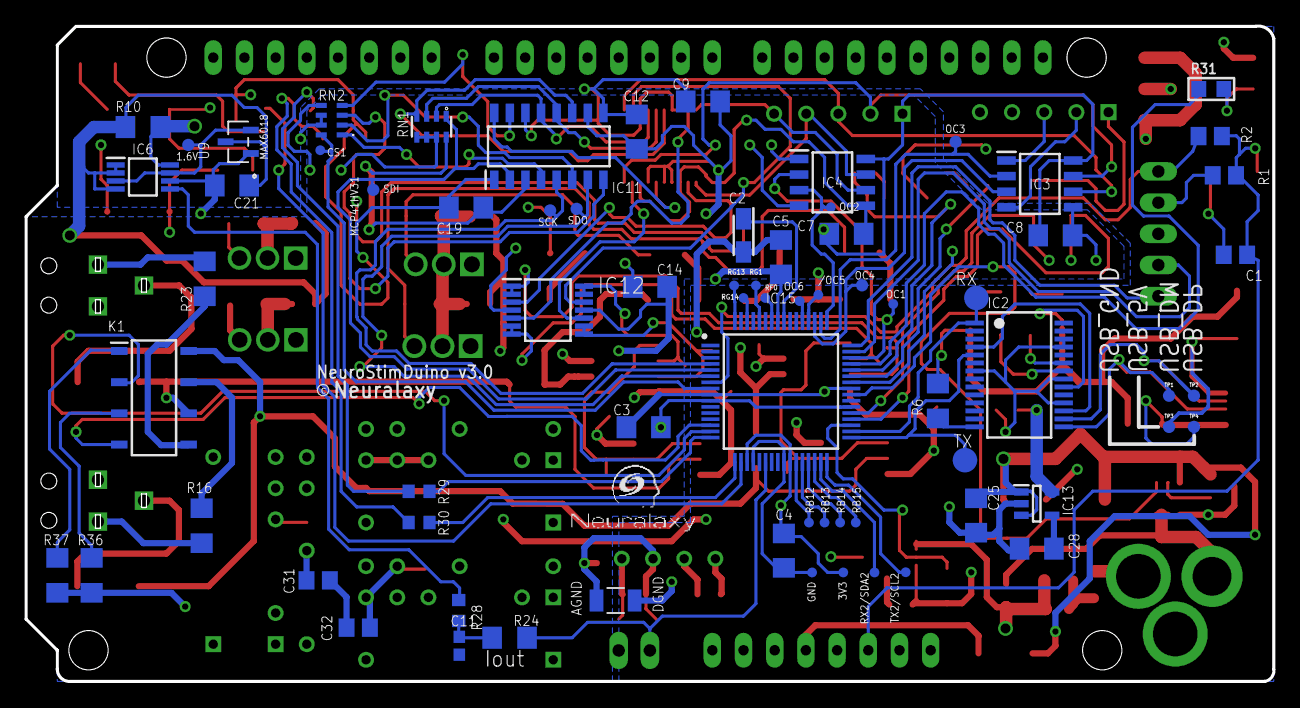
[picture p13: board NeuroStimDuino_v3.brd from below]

Board: 4 copper layers, 101.6 x 53.4 mm, 177 parts (68 on the bottom side), 125 nets.

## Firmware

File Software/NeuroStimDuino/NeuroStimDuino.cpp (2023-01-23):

/*--------------------------------------------------------------------
  NeuroStimDuino.cpp - Arduino Library for controlling NeuroStimDuino using I2C commands.
  Created by: Neuralaxy LLC
  Created on: April 1st, 2021.
  Contact: contactus[at]neuralaxy.com
  
  This library is free software: you can redistribute it and/or modify it under the terms of the GNU Lesser General Public License as published by
  the Free Software Foundation, either version 3 of the License, or (at your option) any later version.
  This library is distributed in the hope that it will be useful, but WITHOUT ANY WARRANTY; without even the implied warranty of MERCHANTABILITY or 
  FITNESS FOR A PARTICULAR PURPOSE.  See the GNU Lesser General Public License for more details <http://www.gnu.org/licenses/>.
--------------------------------------------------------------------*/

#include <Arduino.h>
#include <SerialCommands.h>
#include "NeuroStimDuino.h"

volatile int NSDuino_address = default_i2c_addr;
volatile bool Pulse_Channel_1 = false, Pulse_Channel_2 = false; 

int I2Cwrite(int numbytes, uint8_t commd, uint8_t channel_no = -1, uint8_t data_lsb = -1, uint8_t data_msb = -1){
   int error = -1;
   NSWire.beginTransmission(NSDuino_address);
   NSWire.write(numbytes);
   switch(numbytes){
    case 1:
            NSWire.write(commd);			
            break;
    case 2: 
            NSWire.write(commd);			
            NSWire.write(channel_no);			
            break;
    case 3: 
            NSWire.write(commd);			
            if (channel_no != -1){
              NSWire.write(channel_no);              			  
            }            
            NSWire.write(data_lsb);			
            break;
    case 4: 
            NSWire.write(commd);			
            NSWire.write(channel_no);		
            NSWire.write(data_lsb);			
            NSWire.write(data_msb);			
            break;                      
   }   
   error = NSWire.endTransmission(true);
   return(error); 
}

int I2Cread(int num_bytes){
	int error = -1;
	int reg_value = 0;
	int count = 1;
	NSWire.requestFrom(NSDuino_address, num_bytes); //Request num_bytes from NSDuino
	while(NSWire.available()){
		if (count == 1){
			reg_value = NSWire.read();
			count++;
		}
		else if(count == 2)
		{
			reg_value = (NSWire.read()<<8) + reg_value; 
		}		
	}	
	return (reg_value);
}

char* I2Cread_byte_array(int num_bytes){
	int error = -1;
	static char data_array[20];	//Size must be equal to num_bytes 
	int count = 0;
	int samp_val; 
		 
	NSWire.requestFrom(NSDuino_address, num_bytes); //Request num_bytes from NSDuino	
	while(NSWire.available()){
		data_array[count] = NSWire.read();		
		count++;		
		if(count >= num_bytes){
			//terminate the loop using break statement
			break;
		}		
	}	
	return data_array;
}

enum I2Ccommand str2enum (const char* reg)
{
	if(!strcmp(reg, "AMPL"))
		return AMPL;
	else if(!strcmp(reg, "FREQ"))
		return FREQ;
	else if(!strcmp(reg, "DURN"))
		return DURN;
	else if(!strcmp(reg, "IDLY"))
		return IDLY;
	else if(!strcmp(reg, "DELY"))
		return DELY;
	else if(!strcmp(reg, "SYMM"))
		return SYMM;
	else if(!strcmp(reg, "ENAB"))
		return ENAB;
	else if(!strcmp(reg, "RAMP"))
		return RAMP;
	else
		return ERR; // reg not found
}

//This is the default handler, and gets called when no other command matches. 
void cmd_unrecognized(SerialCommands* sender, const char* cmd)
{
  sender->GetSerial()->print("Unrecognized command [");
  sender->GetSerial()->print(cmd);
  sender->GetSerial()->println("]");
}

//called for ON command
void cmd_led_on(SerialCommands* sender)
{
  digitalWrite(ArduinoLedPin, HIGH);  
  sender->GetSerial()->println("Led is on");
}

//called for OFF command
void cmd_led_off(SerialCommands* sender)
{
  digitalWrite(ArduinoLedPin, LOW);  
  sender->GetSerial()->println("Led is off");
}

void setAmplitude_Callback(SerialCommands* sender)
{
  int i2c_error = -1; 
  char* chan_str = sender->Next();
  if (chan_str == NULL)
  {
    sender->GetSerial()->println("ERROR! Channel # is missing ");
    return;
  }
  int chan = atoi(chan_str);
  
  char* val_str = sender->Next();
  if (val_str == NULL)
  {
    sender->GetSerial()->println("ERROR! Amplitude is missing ");
    return;
  }
  float valf = atof(val_str); //int val = atoi(val_str);
  if (valf < AMPL_LOW_LIMIT || valf > AMPL_UPP_LIMIT)
  {
    sender->GetSerial()->println("ERROR! Value outside range ");
    return;
  }
  //Convert stim amplitude from milliAmps to digital potentiometer counts (0-127)
  int val = round(valf/current_conversion_ratio);
  i2c_error = I2Cwrite(ThreeBytesCommds, AMPL, chan, val); 
  if (i2c_error != 0){
    sender->GetSerial()->print("I2C error = ");
    sender->GetSerial()->println(i2c_error);   
  }
  delay(3); // Required for dsPIC to finish processing I2C write command
  // Now read the register value
  val = I2Cread(1);	
  //Convert stim amplitude from digital potentiometer count to milliAmps
  valf = val*current_conversion_ratio; //val = ceil(val*current_conversion_ratio);
  sender->GetSerial()->print("Channel ");
  sender->GetSerial()->print(chan);
  sender->GetSerial()->print(", amplitude is set to ");
  sender->GetSerial()->print(valf,3);					
  sender->GetSerial()->println(" mA");
}

void setFrequency_Callback(SerialCommands* sender)
{
  int i2c_error = -1; 
  char* chan_str = sender->Next();
  if (chan_str == NULL)
  {
    sender->GetSerial()->println("ERROR! Channel # is missing ");
    return;
  }
  int chan = atoi(chan_str);
  
  char* val_str = sender->Next();
  if (val_str == NULL)
  {
    sender->GetSerial()->println("ERROR! Frequency is missing ");
    return;
  }
  int val = atoi(val_str);
  if (val < FREQ_LOW_LIMIT || val > FREQ_UPP_LIMIT)
  {
    sender->GetSerial()->println("ERROR! Value outside range ");
    return;
  }
  i2c_error = I2Cwrite(ThreeBytesCommds, FREQ, chan, val); 
  if (i2c_error != 0){
    sender->GetSerial()->print("I2C error = ");
    sender->GetSerial()->println(i2c_error);   
  }

  delay(3); // Required for dsPIC to finish processing I2C write command
  // Now read the register value
  val = I2Cread(1);	
  sender->GetSerial()->print("Channel ");
  sender->GetSerial()->print(chan);
  sender->GetSerial()->print(", frequency is set to ");
  sender->GetSerial()->print(val);	
  sender->GetSerial()->println(" Hz");  
}

void setPulseDuration_Callback(SerialCommands* sender)
{
  int i2c_error = -1; 
  uint8_t val_lsb = 0;
  uint8_t val_msb = 0;
  
  char* chan_str = sender->Next();
  if (chan_str == NULL)
  {
    sender->GetSerial()->println("ERROR! Channel # is missing ");
    return;
  }
  int chan = atoi(chan_str);
  
  char* val_str = sender->Next();
  if (val_str == NULL)
  {
    sender->GetSerial()->println("ERROR! Duration is missing ");
    return;
  }
  int val = atoi(val_str);
  if (val < DURN_LOW_LIMIT || val > DURN_UPP_LIMIT)
  {
    sender->GetSerial()->println("ERROR! Value outside range ");
    return;
  }
  //Convert int to 2 bytes with LSB byte first
  val_lsb = (val & 255);
  val_msb = ((val >> 8) & 255);
  i2c_error = I2Cwrite(FourBytesCommds, DURN, chan, val_lsb, val_msb); 
  if (i2c_error != 0){
    sender->GetSerial()->print("I2C error = ");
    sender->GetSerial()->println(i2c_error);   
  }
  delay(3); // Required for dsPIC to finish processing I2C write command
  // Now read the register value
  val = I2Cread(2);	
  sender->GetSerial()->print("Channel ");
  sender->GetSerial()->print(chan);
  sender->GetSerial()->print(", pulse duration is set to ");
  sender->GetSerial()->print(val);					  
  sender->GetSerial()->println(" uSec");
}

void setInterPhaseDelay_Callback(SerialCommands* sender)
{
  int i2c_error = -1; 
  char* chan_str = sender->Next();
  if (chan_str == NULL)
  {
    sender->GetSerial()->println("ERROR! Channel # is missing ");
    return;
  }
  int chan = atoi(chan_str);
  
  char* val_str = sender->Next();
  if (val_str == NULL)
  {
    sender->GetSerial()->println("ERROR! Inter-phase duration is missing ");
    return;
  }
  int val = atoi(val_str);
  if (val < IDLY_LOW_LIMIT || val > IDLY_UPP_LIMIT)
  {
    sender->GetSerial()->println("ERROR! Value outside range ");
    return;
  }
  i2c_error = I2Cwrite(ThreeBytesCommds, IDLY, chan, val); 
  if (i2c_error != 0){
    sender->GetSerial()->print("I2C error = ");
    sender->GetSerial()->println(i2c_error);   
  }
  delay(3); // Required for dsPIC to finish processing I2C write command
  // Now read the register value
  val = I2Cread(1);	
  sender->GetSerial()->print("Channel ");
  sender->GetSerial()->print(chan);
  sender->GetSerial()->print(", inter-phase duration is set to ");
  sender->GetSerial()->print(val);	
  sender->GetSerial()->println(" uSec");
}

void setStartDelay_Callback(SerialCommands* sender)
{
  int i2c_error = -1; 
  char* chan_str = sender->Next();
  if (chan_str == NULL)
  {
    sender->GetSerial()->println("ERROR! Channel # is missing ");
    return;
  }
  int chan = atoi(chan_str);
  
  char* val_str = sender->Next();
  if (val_str == NULL)
  {
    sender->GetSerial()->println("ERROR! Start delay is missing ");
    return;
  }
  int val = atoi(val_str);
  if (val < DELY_LOW_LIMIT || val > DELY_UPP_LIMIT)
  {
    sender->GetSerial()->println("ERROR! Value outside range ");
    return;
  }
  i2c_error = I2Cwrite(ThreeBytesCommds, DELY, chan, val); 
  if (i2c_error != 0){
    sender->GetSerial()->print("I2C error = ");
    sender->GetSerial()->println(i2c_error);   
  }

  delay(3); // Required for dsPIC to finish processing I2C write command
  // Now read the register value
  val = I2Cread(1);	
  sender->GetSerial()->print("Channel ");
  sender->GetSerial()->print(chan);
  sender->GetSerial()->print(", start delay is set to ");
  sender->GetSerial()->print(val);	
  sender->GetSerial()->println(" mSec");
}

void setWaveformSymmetry_Callback(SerialCommands* sender)
{
  int i2c_error = -1; 
  char* chan_str = sender->Next();
  if (chan_str == NULL)
  {
    sender->GetSerial()->println("ERROR! Channel # is missing ");
    return;
  }
  int chan = atoi(chan_str);
  
  char* val_str = sender->Next();
  if (val_str == NULL)
  {
    sender->GetSerial()->println("ERROR! Value is missing ");
    return;
  }
  int val = atoi(val_str);
  if (val != 0 && val != 1)
  {
    sender->GetSerial()->println("ERROR! Value outside range ");
    return;
  }
  i2c_error = I2Cwrite(ThreeBytesCommds, SYMM, chan, val); 
  if (i2c_error != 0){
    sender->GetSerial()->print("I2C error = ");
    sender->GetSerial()->println(i2c_error);   
  }

  delay(3); // Required for dsPIC to finish processing I2C write command
  // Now read the register value
  val = I2Cread(1);	
  sender->GetSerial()->print("Channel ");
  sender->GetSerial()->print(chan);
  sender->GetSerial()->print(", pulse shape is set to ");
  if (val == 1){
	sender->GetSerial()->println("symmetrical");  
  }else{
	sender->GetSerial()->println("asymmetrical");  
  }  
}
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

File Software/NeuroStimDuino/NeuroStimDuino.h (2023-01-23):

/*--------------------------------------------------------------------
  NeuroStimDuino.h - Arduino Library for controlling NeuroStimDuino using I2C commands.
  Created by: Neuralaxy LLC
  Created on: April 1st, 2021.
  Contact: contactus[at]neuralaxy.com
  
  This library is free software: you can redistribute it and/or modify it under the terms of the GNU Lesser General Public License as published by
  the Free Software Foundation, either version 3 of the License, or (at your option) any later version.
  This library is distributed in the hope that it will be useful, but WITHOUT ANY WARRANTY; without even the implied warranty of MERCHANTABILITY or 
  FITNESS FOR A PARTICULAR PURPOSE.  See the GNU Lesser General Public License for more details <http://www.gnu.org/licenses/>.
--------------------------------------------------------------------*/

#ifndef NeuroStimDuino_h
#define NeuroStimDuino_h

#include <Arduino.h>
#include <SerialCommands.h>
#include <Wire.h>

#if defined(__AVR_ATmega1280__) || defined(__AVR_ATmega2560__)
  //For Arduino Mega  
  #define NSWire Wire
    
#elif defined(__SAM3X8E__)
  //For Ardunio Due
  #define NSWire Wire1

#else
  //For anyone else
  #define NSWire Wire

#endif 

#define default_i2c_addr 0x1A
#define FourBytesCommds 4
#define ThreeBytesCommds 3 
#define TwoBytesCommds 2
#define OneByteCommds 1
#define AMPL_UPP_LIMIT  31	//31 milliAmps max
#define AMPL_LOW_LIMIT  0
#define FREQ_UPP_LIMIT  100
#define FREQ_LOW_LIMIT  3
#define DURN_UPP_LIMIT  2000
#define DURN_LOW_LIMIT  7	//Clock resolution is 6.4us, hence minimum allowed is 7 us
#define IDLY_UPP_LIMIT  255
#define IDLY_LOW_LIMIT  0
#define DELY_UPP_LIMIT  165  //50% of max. possible @3Hz stim frequency, 
#define DELY_LOW_LIMIT  0
#define ADDR_UPP_LIMIT  119
#define ADDR_LOW_LIMIT  8


const int ArduinoLedPin = 13;
const int Data_samples_size = 100;
const float current_conversion_ratio = 0.24; // 0.24 mA/(digiPOT_count) 
extern volatile int NSDuino_address;
extern volatile bool Pulse_Channel_1, Pulse_Channel_2; 

enum I2Ccommand {
	ERR  = 0x00,    
    AMPL = 0x01,
    FREQ = 0x02,
    DURN = 0x03,
    IDLY = 0x04,
    DELY = 0x05,
    SYMM = 0x06,
    ADDR = 0x07,
    SAMP = 0x08,
    READ = 0x09,
    RSET = 0x0A,
    EOFF = 0x0F,
    STIM = 0x10,
    STOP = 0x12,
    ENAB = 0x14,
	RAMP = 0x1B,
    WAIT = 0x20		//unimplemented
};

void cmd_led_on(SerialCommands* );
void cmd_led_off(SerialCommands* );
void setAmplitude_Callback(SerialCommands* );
void setFrequency_Callback(SerialCommands* );
void setPulseDuration_Callback(SerialCommands* );
void setInterPhaseDelay_Callback(SerialCommands* );
void setStartDelay_Callback(SerialCommands* );
void setWaveformSymmetry_Callback(SerialCommands* );
void changeI2Caddress_Callback(SerialCommands* );
void resetNeuroStimDuino_Callback(SerialCommands* );
void startStimulation_Callback(SerialCommands* );
void stopStimulation_Callback(SerialCommands* );
void enableChannel_Callback(SerialCommands* );
void setEmergencyOFF_Callback(SerialCommands* );
void startCurrentSampling_Callback(SerialCommands* );
void startPulse_Callback(SerialCommands* );
void readRegister_Callback(SerialCommands* );
void enableRamping_Callback(SerialCommands* );
void cmd_unrecognized(SerialCommands* , const char* );
void print_Channel_Parameters(int );
void startStimulationPulse(int );
int I2Cwrite(int , uint8_t , uint8_t , uint8_t , uint8_t );
int I2Cread(int ); 
char* I2Cread_byte_array(int );

enum I2Ccommand str2enum (const char* );

/*
class NeuroStimDuino
{
  public:
    NeuroStimDuino(uint8_t addr);
    //int I2Cwrite(int numbytes, I2Ccommand comm, uint8_t channel_no, int data1, int data2);    
    int I2Cread();
                
  private:
    uint8_t _i2caddr;
};
*/
#endif

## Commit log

2021-03-12 NeuroStimDuino v1.0 schematic and PCB
    [NeuroStimDuino.brd, NeuroStimDuino.sch]
2021-04-21 Sample stimulation current using on-board sensor
2021-06-01 NeuroStimDuino_v1.1 schematic and PCB files
    [NeuroStimDuino.brd, NeuroStimDuino.sch]
2021-10-04 hex file for PIC controller on-board NeuroStimDuino
    1. Foe these steps for loading a pre-built hex file, without compiling the source code: https://www.youtube.com/watch?v=pEMORwwuyos
    2. Select microcontroller as dsPIC33FJ256GP506A
2021-10-13 Read current sensor and register values using I2C
2021-11-01 Added current_conversion_ratio and routine house keeping
2021-11-15 Allows user to input floating point current amplitude via "AMPL" command
2021-12-07 Add BOM and pick n place files
    [Bill_of_Materials_NeuroStimDuino_v1_1.xlsx, PnP_back_NeuroStimDuino_v1_1.csv, PnP_front_NeuroStimDuino_v1_1.csv]
2023-01-21 Added pin diagram and layout for NSDuino2.1
2023-01-23 Add RAMP command, increase current limit to 31mA
2023-01-23 Added board layout and pinout
2023-03-30 Added Gerber files for NeuroStimDuino_v2.1
    [Milling.gbr, copper_bottom_l4.gbr, copper_inner_l2.gbr, copper_inner_l3.gbr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]
2023-03-30 Eagle files of NSDuino v1.1
    [Bill_of_Materials_NeuroStimDuino_v1_1.xlsx, NeuroStimDuino_v1_1.brd, NeuroStimDuino_v1_1.sch, PnP_back_NeuroStimDuino_v1_1.csv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]
2023-03-30 Eagle files for NSDuino_v2.1
    [NeuroStimDuino_2.1_BOM.xlsx, NeuroStimDuino_v2.brd, NeuroStimDuino_v2.sch, PnP_NeuroStimDuino_v2_1_back.csv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]
2024-09-11 Add HEX file for v2.1 board
2026-03-12 Added NeuroStimDuino v3.1 EAGLE schematics+PCB
    [NeuroStimDuino_v3.brd, NeuroStimDuino_v3.sch, NeuroStimDuino_v3_BOM.xlsx, PnP_NeuroStimDuino_v3_back.csv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]

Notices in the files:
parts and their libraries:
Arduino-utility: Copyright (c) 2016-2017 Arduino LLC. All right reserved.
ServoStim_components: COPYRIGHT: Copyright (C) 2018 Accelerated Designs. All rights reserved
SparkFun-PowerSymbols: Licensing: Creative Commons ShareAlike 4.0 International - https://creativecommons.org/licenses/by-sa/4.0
